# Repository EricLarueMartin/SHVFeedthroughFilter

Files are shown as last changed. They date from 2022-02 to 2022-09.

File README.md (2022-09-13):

# SHVFeedthroughFilter
Coaxial feedthrough filter that mounts on an SHV bulkhead.

SHV bulkhead connectors on both ends allow mounting the filter such that the body of the filter is on either side of the bulkhead, which may be helpful for space constraints.

Uses commercially available parts to make a high voltage filter that fits on a standard SHV bulkhead connector.
This filter was designed for use biasing cryogenically cooled solid state detectors, which have very low leakage current making high resistance series elements suitable.

Resistors are axial lead able to handle the high voltage while the sides of the resistor body are near ground, such as Ohmite MOX112523*. Though a shorter resistor would work the stray capacitance is important to performance and this model has the lowest stray capacitance at 0.25 pF.

Connector used for protoype was TE Connectivity AMP Connectors 5225059-3, this is out of production and an alternative will become necessary when stocks depleate. The BM61482 from Bracke Manufacturing appears to be a direct replacement. 

Capacitors are 6kV 2225 package, such as Vishay Vitramon HV2225*. Six 2.7 nF capacitors were used for the prototype, but three high capacitance X7R capacitors and three lower capacitance C0G capacitors would likely result in better high frequency performance.

The center piece for the capacitors to solder to is a brass standoff, 6 mm hex diameter and up to 6mm height.

The tube is a 0.686 inch ID brass or copper tube. A 3/4 inch 0.032 inch wall tube is readily available and suitable.

A bleeder resistor on the load side of this filter will result in voltage drop across the series resistors. Bleeder resistors are not required if stored energy is under 10 J. 

The prototype filter used six 2.7 nF capacitors, which will only result in 0.3 J of stored energy at 6 kV. With 100 Mohm series resistors the maximum current the filter can produce is only 60 microamps at 6 kV, which is negligible compared to the ~10 mA requires to produce a dangerous shock. With 0.25 pF of parallel capacitance this high of a resistance isn't effective at frequencies above 10 kHz. 5 Mohm resistors would still limit the current from a shock to ~ 1 mA and performance at power distribution frequencies would still be better than 100 dB.

The cable ground of the recommended connector acts as a guard ring to reduce the effective capacitance between leads of the axial resistors, this stray capacitance dominates filter performance in the GHz range. A guard ring is added using washers for the second stage resistor.

This version includes a second capacitor stage with a pulse line. This allows pulsing through the HV line and also provides source termination at the filter, which can help reduce noise that is picked up on the HV line after the filter.

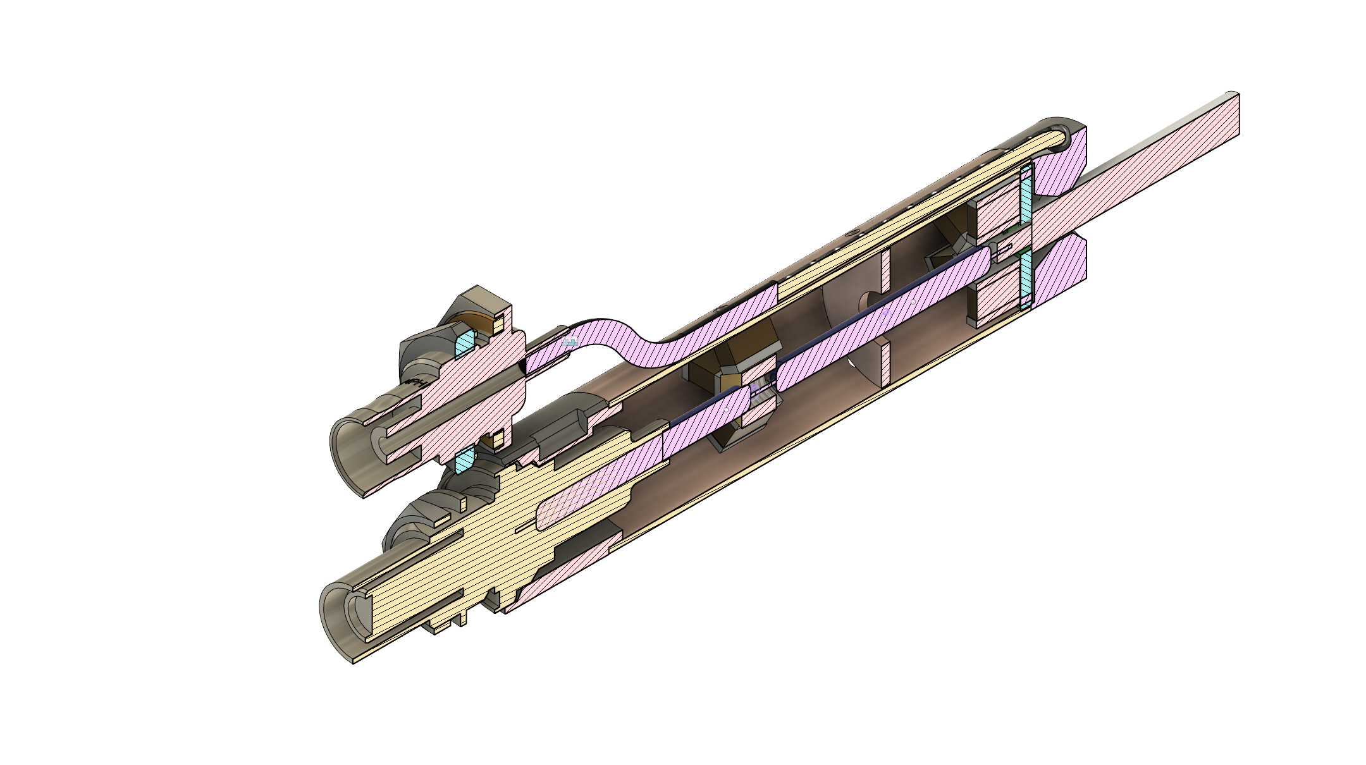
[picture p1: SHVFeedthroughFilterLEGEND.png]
SHV to SHV Feedthrough Filter


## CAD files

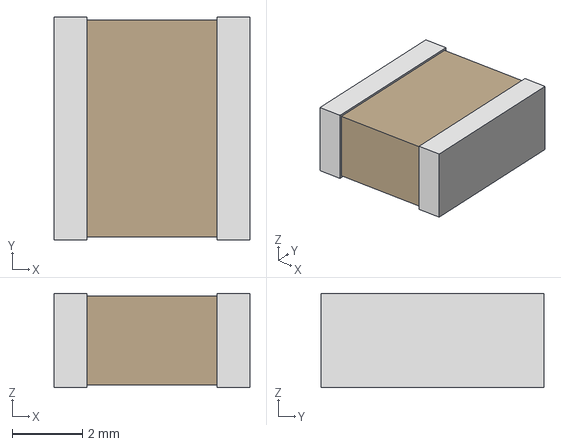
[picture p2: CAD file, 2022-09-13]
DesignFiles/SHV_Feedthrough_PulserPCB/CAP_HV2225_VIS.step
5.59 x 6.35 x 2.69 mm

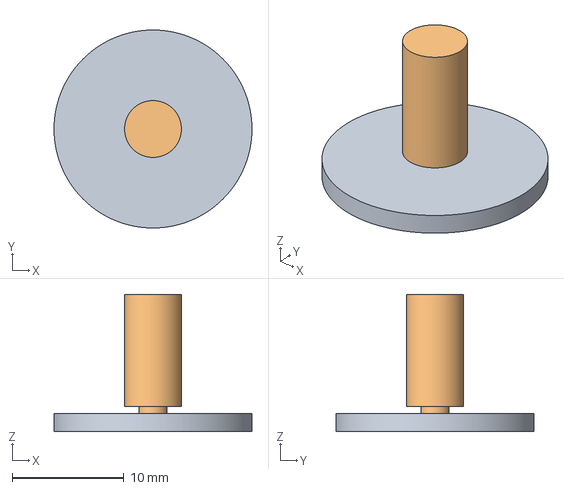
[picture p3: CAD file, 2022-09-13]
EpoxytestJig.3mf
17.7 x 17.7 x 12.3 mm
Shape-Cylinder x 2

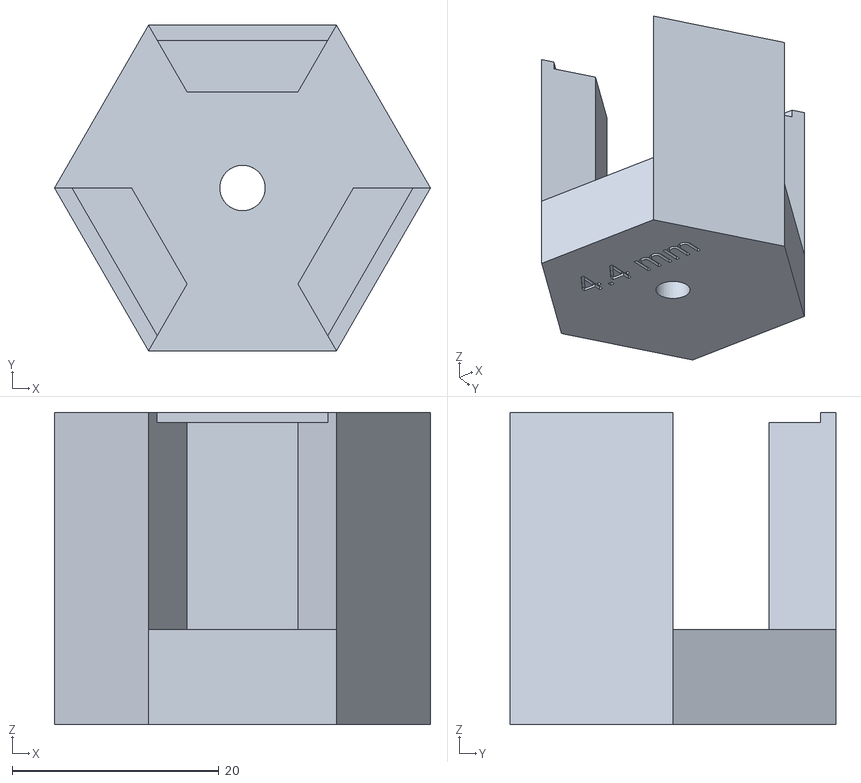
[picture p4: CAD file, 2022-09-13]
FabricationFiles/ResistorJig4.4mm.stl
36.4 x 31.5 x 30.2

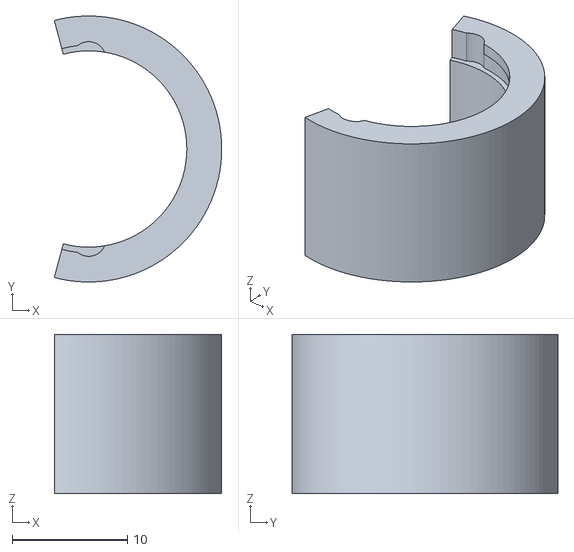
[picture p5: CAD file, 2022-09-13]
FabricationFiles/EndAlignmentJig.stl
14.5 x 23.0 x 13.8

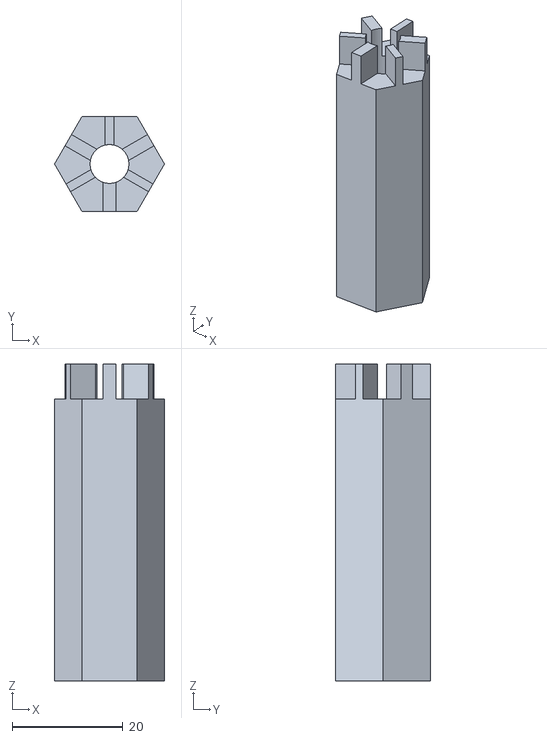
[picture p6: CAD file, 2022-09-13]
FabricationFiles/CapacitorRemovalJig.stl
19.8 x 17.2 x 57.1

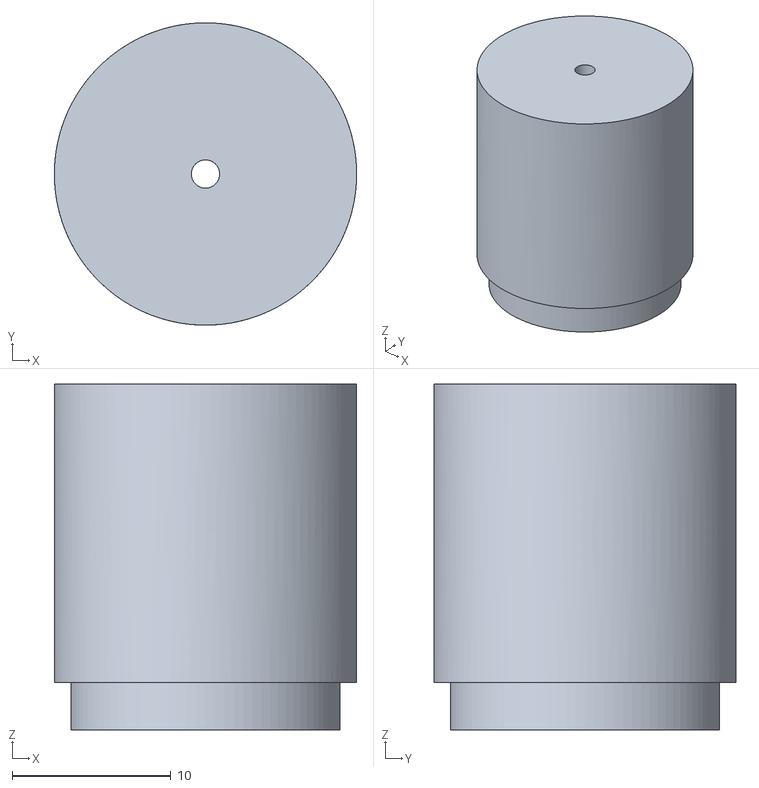
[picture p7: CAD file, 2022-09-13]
FabricationFiles/PinPositioningDuringEndCapAttachmentJig.stl
19.0 x 19.0 x 21.8

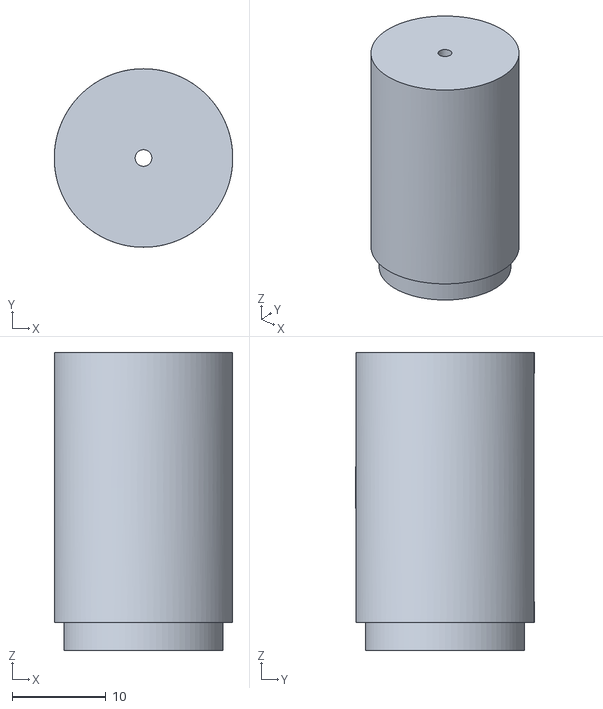
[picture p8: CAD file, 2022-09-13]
FabricationFiles/PinPositionCheckJig.stl
19.0 x 19.0 x 31.8

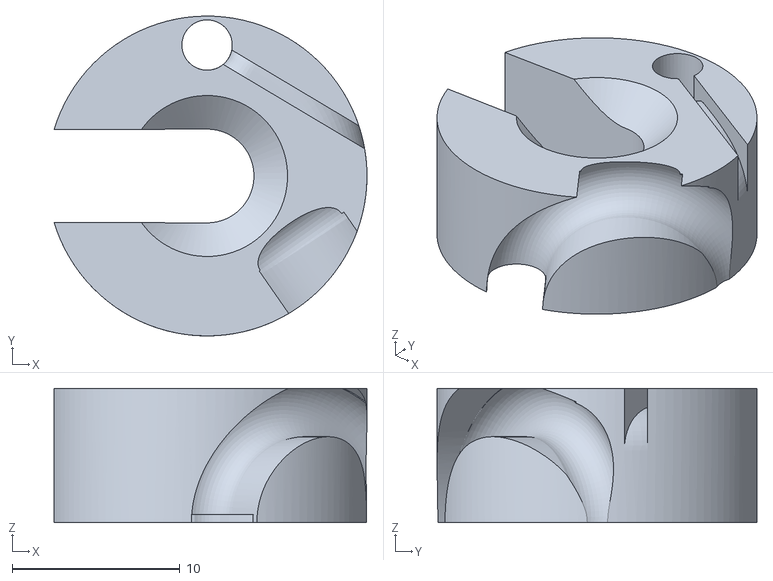
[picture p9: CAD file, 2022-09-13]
FabricationFiles/EndCap.stl
18.6 x 19.0 x 8.00

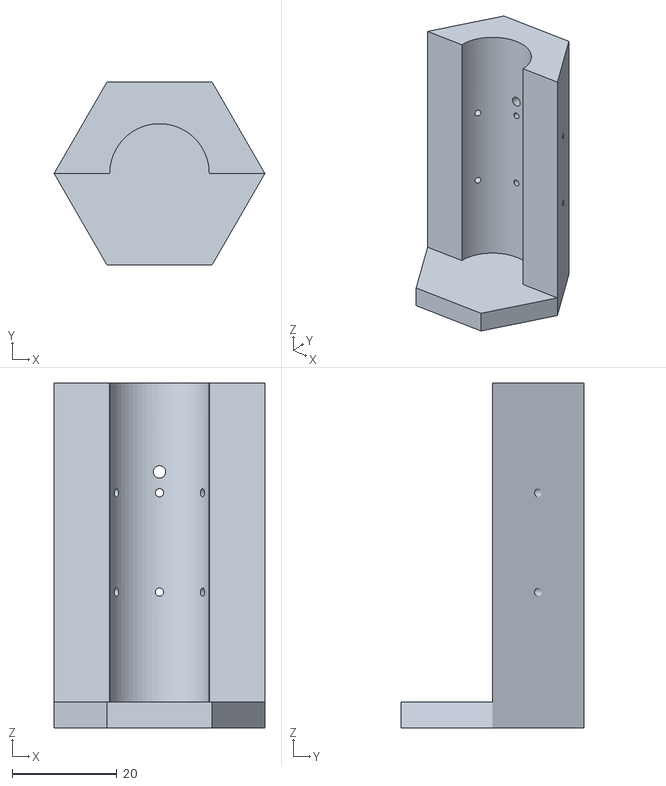
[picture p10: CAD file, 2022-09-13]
FabricationFiles/TwoPartTubeJigA.stl
40.3 x 34.9 x 66.0

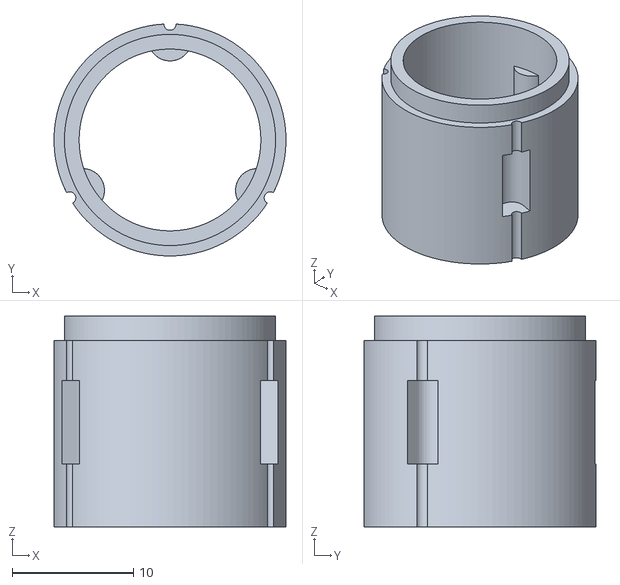
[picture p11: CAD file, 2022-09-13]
FabricationFiles/TubeInsulator+0.4mm.stl
19.1 x 19.1 x 17.4

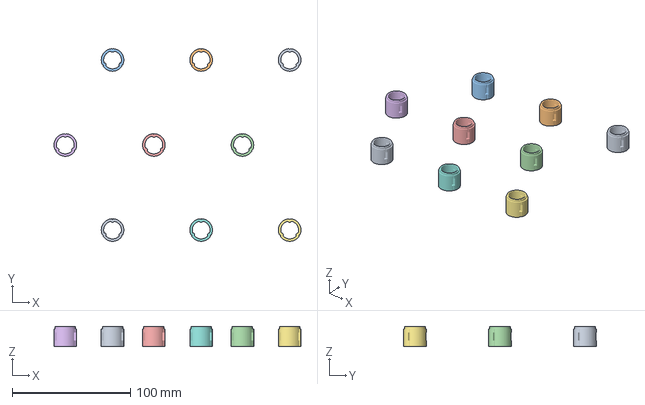
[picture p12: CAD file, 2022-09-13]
FabricationFiles/TubeInsulatorx9.3mf
209.1 x 163.1 x 17.0 mm

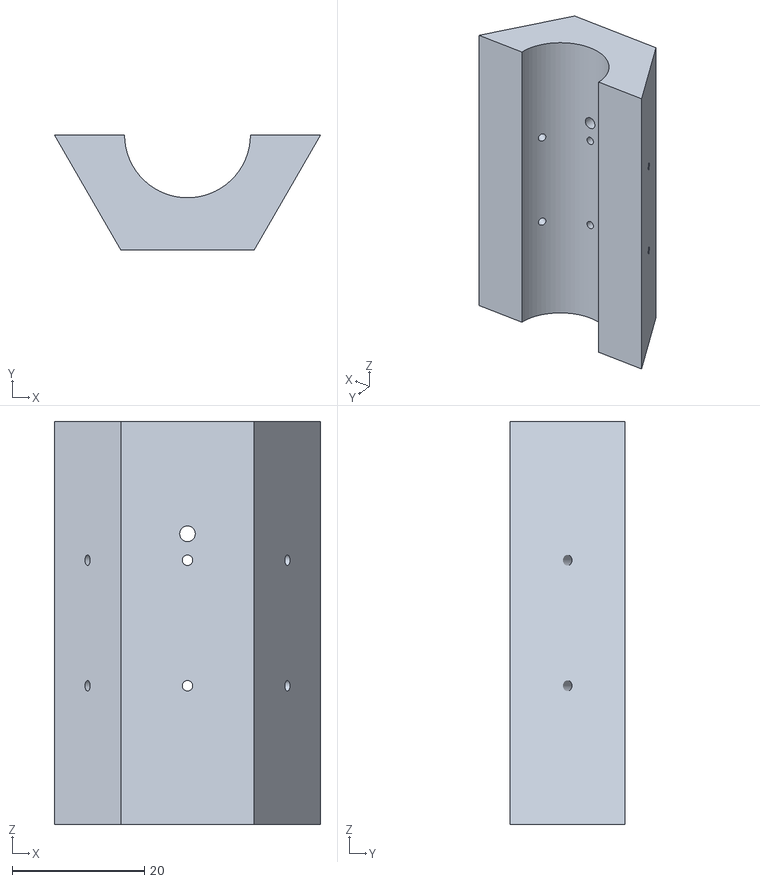
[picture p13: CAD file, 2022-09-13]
FabricationFiles/TwoPartTubeJigB.stl
40.3 x 17.5 x 61.0

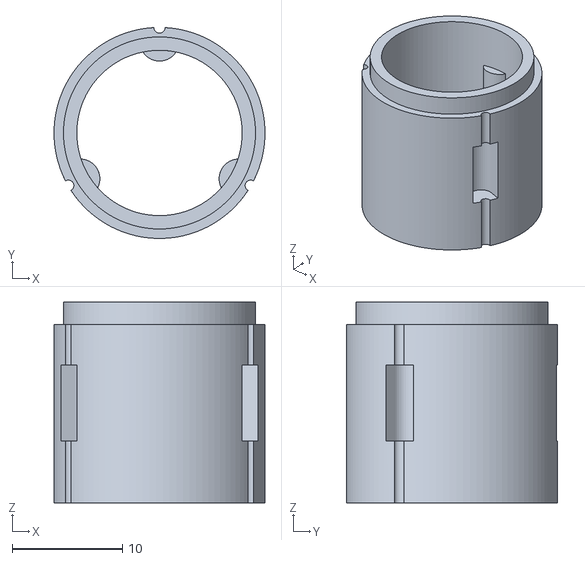
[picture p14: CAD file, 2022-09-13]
FabricationFiles/TubeInsulator+1.2mm.stl
19.1 x 19.1 x 18.2

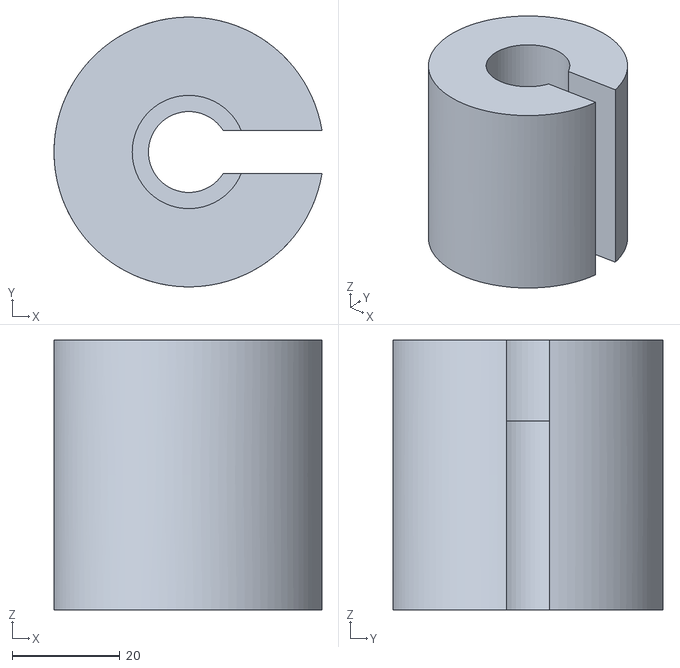
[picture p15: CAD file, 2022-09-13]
FabricationFiles/PottingStand.stl
49.7 x 50.0 x 50.0

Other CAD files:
FabricationFiles/ResistorJig4.0mm.stl
FabricationFiles/TubeInsulator.stl
FabricationFiles/TubeInsulator-2.0mm.stl
FabricationFiles/AluminumCapacitorJig.step
DesignFiles/SHVFeedthroughFilterWithPulseLine_LEGEND60.f3z
FabricationFiles/StandoffCuttingJig.stl
FabricationFiles/TubeInsulator+0.8mm.stl
FabricationFiles/TubeInsulator-0.4mm.stl
FabricationFiles/TubeInsulator-0.8mm.stl

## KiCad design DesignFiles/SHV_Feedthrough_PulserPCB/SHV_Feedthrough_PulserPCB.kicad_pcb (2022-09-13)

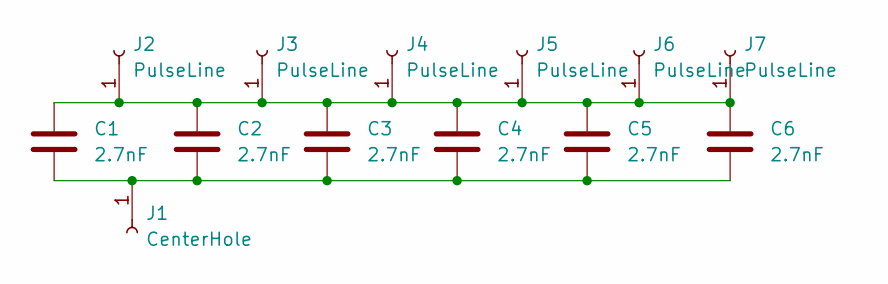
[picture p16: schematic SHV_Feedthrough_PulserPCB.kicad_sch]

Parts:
C1, C2, C3, C4, C5, C6: 2.7nF; HV2225SideMount
J1: CenterHole; MountingHole_2.1mm
J2, J3, J4, J5, J6, J7: PulseLine; RG-174MinHole

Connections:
unnamed: C1.1, C2.1, C3.1, C4.1, C5.1, C6.1, J2.1, J3.1, J4.1, J5.1, J6.1, J7.1
unnamed: C1.2, C2.2, C3.2, C4.2, C5.2, C6.2, J1.1

Board: 2 copper layers, 13 parts (0 on the bottom side), 2 nets, no tracks yet.

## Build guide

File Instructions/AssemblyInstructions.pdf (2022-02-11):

SHV coaxial feedthrough RCR lter
This details how to construct an SHV feedthrough lter using two high voltage series resistors and six parallel capacitors to ground. This lter is intended for use biasing germanium detectors for the LEGEND experiment where the load current is expected to be < 1 nA and a large series resistance is acceptable. The nal lter characteristics are 100 MΩ input resistance, 100 MΩ output resistance, and 16 nF capacitance to ground. The expected capacitance between input and output is 0.13 pF. The lter is constructed to minimize radiation power transfer by keeping the input on the same axis as the output, having the ground current symmetric about the output axis so grounding bypass capacitor radiation is canceled and is emitted perpendicular to the output axis. The entire lter is contained in a sealed tube that mounts on a front-side nut SHV bulkhead jack, which can be lled with oil.
Parts:
- 1 SHV bulkhead jack, TE Connectivity AMP Connectors 5225059-3
- 1 3/4 OD 0.032 wall copper 101 tube cut to 3.16
- 6 2.7 nF 6 kV ceramic capacitors, Vishay Vitramon HV2225Y272KX6ATHV
- 1 0.625 OD 0.26 ID copper washer 1
- 1 5.5 mm brass hex stando cut to 0.25 1
- 2 100 MΩ 7.5 kV axial lead resistors, Ohmite MOX1125231006FE

1

1Appropriate sizes for some components were unavailable.

1

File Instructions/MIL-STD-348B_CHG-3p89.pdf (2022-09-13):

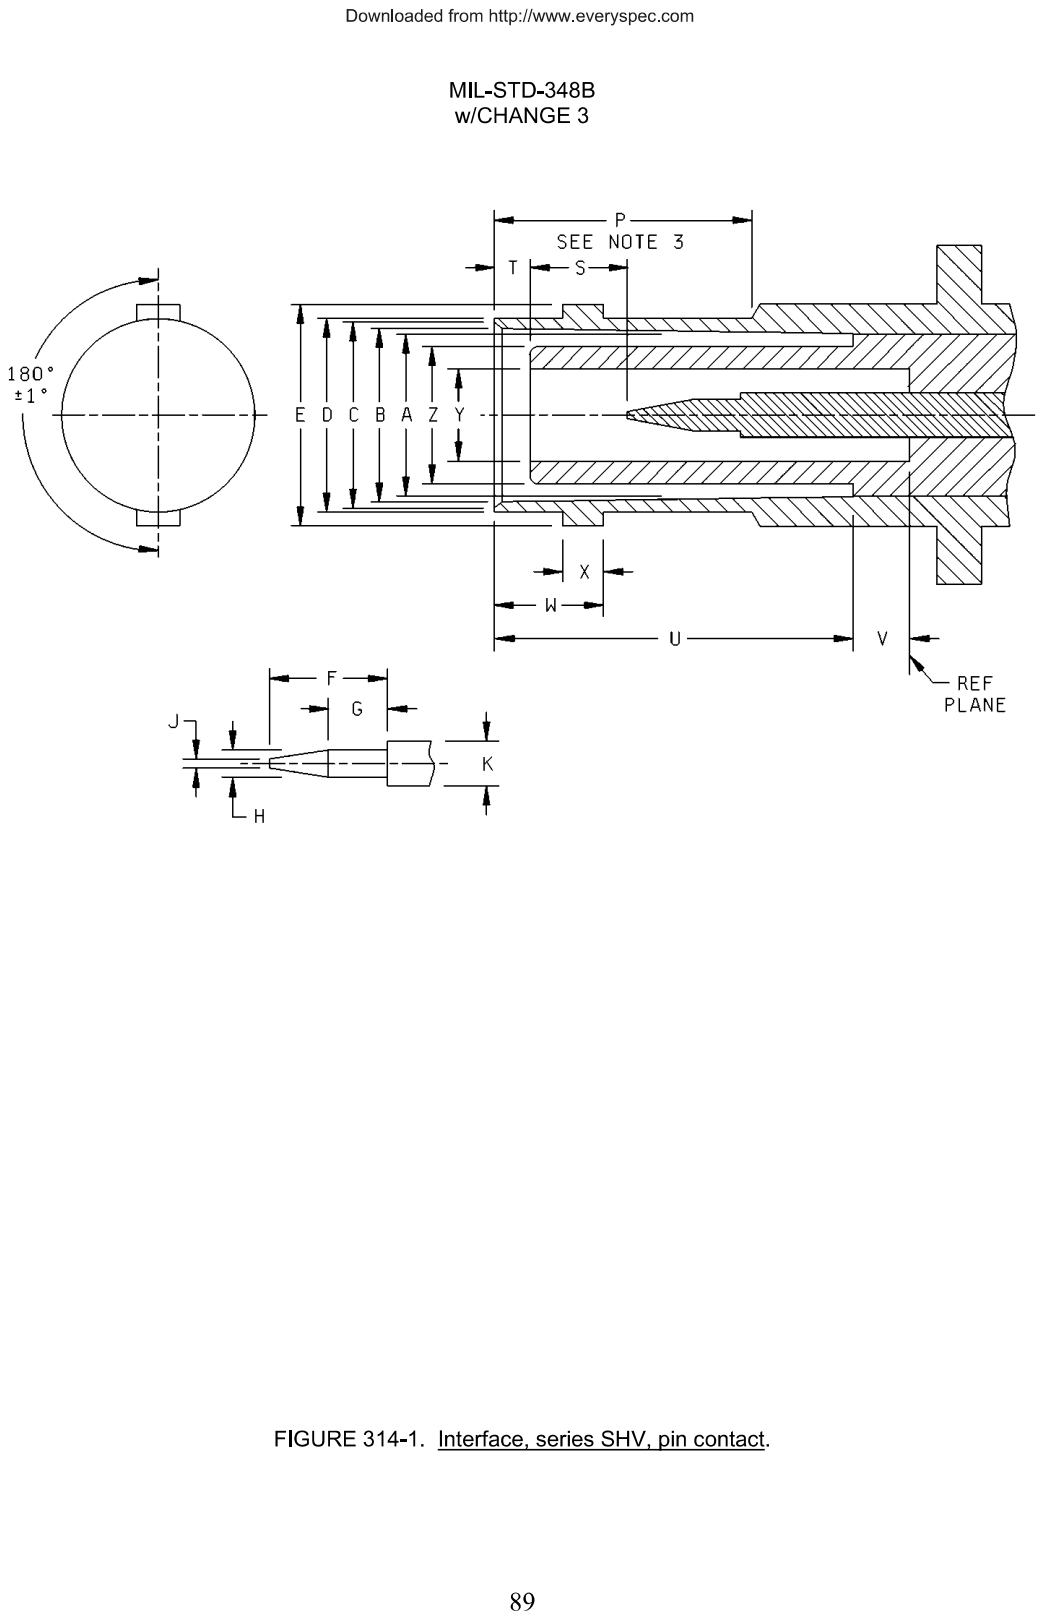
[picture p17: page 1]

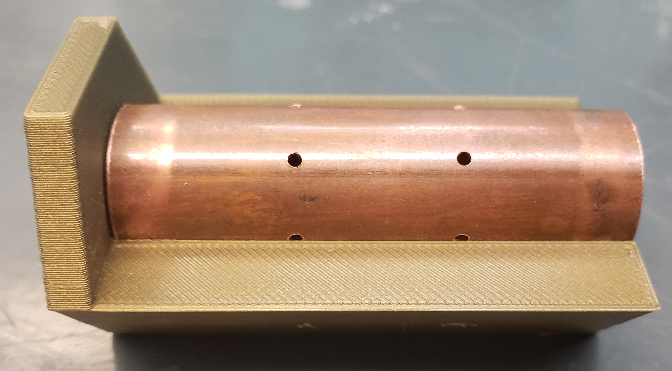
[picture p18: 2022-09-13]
Instructions/TubeRotatedInJig.jpg

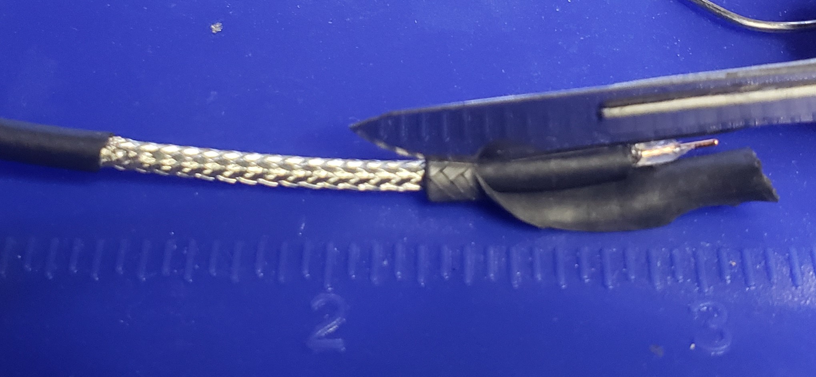
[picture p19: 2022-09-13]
Instructions/TrimmingJacketOffCable.jpg

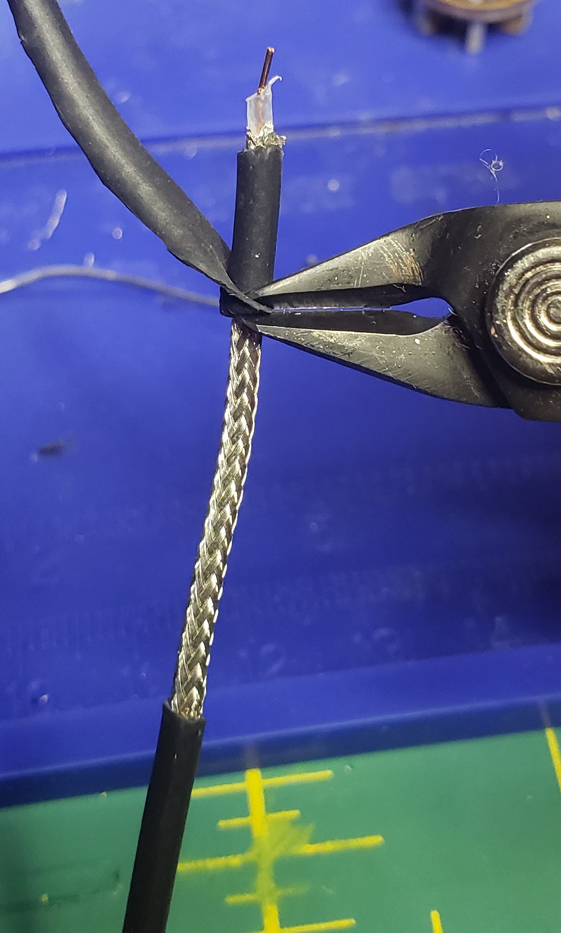
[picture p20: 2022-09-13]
Instructions/ClippingJacket.jpg

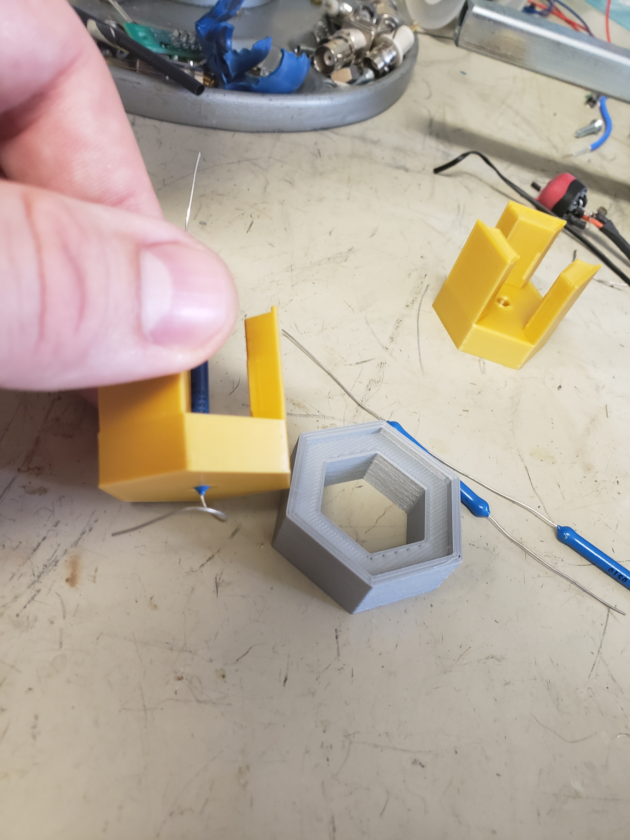
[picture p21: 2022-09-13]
Instructions/ResistorSpringLead.jpg

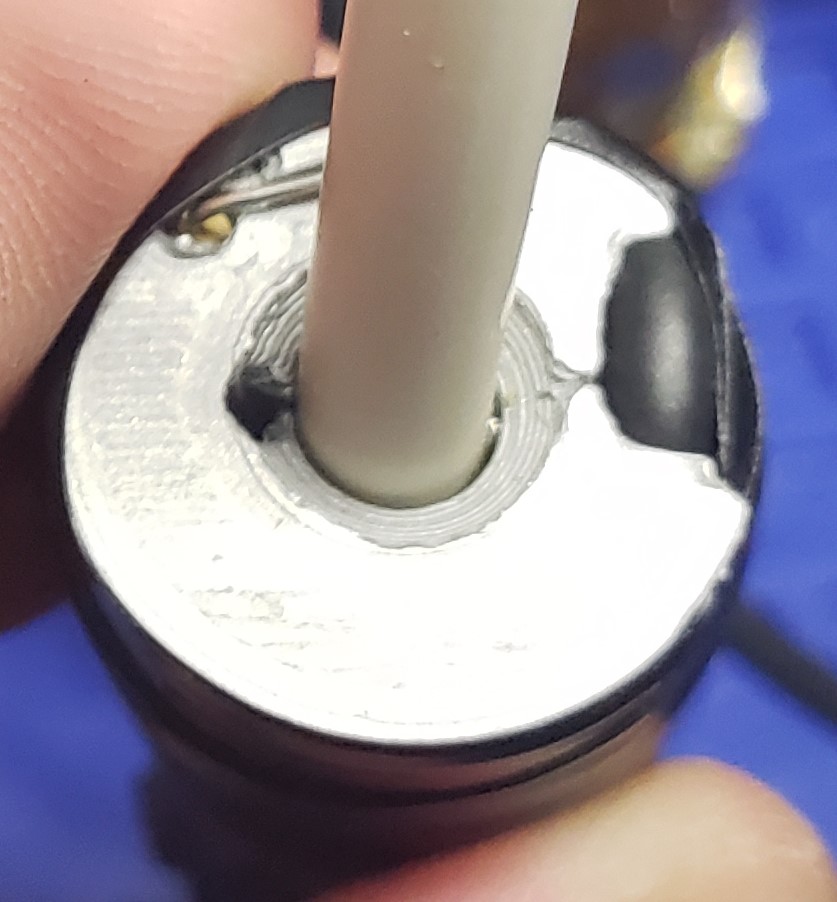
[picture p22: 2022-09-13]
Instructions/EndCapFillPort.jpg

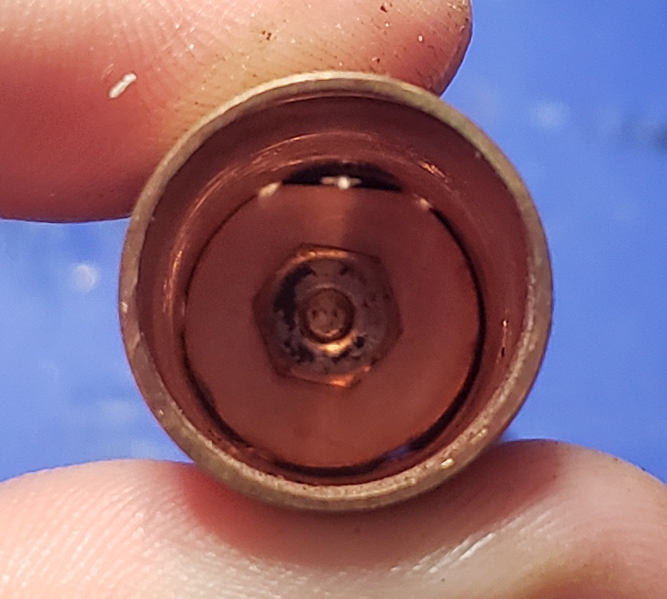
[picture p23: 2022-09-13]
Instructions/WasherRotation.jpg

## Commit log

2022-02-08 Added jigs.
    [2PartTubeJig.f3d, CapacitorJig.f3d, SHVFeedthroughFilter v8.f3z, SHVFeedthroughFilter.f3z]
2022-02-10 Added STLs for jigs, data sheets, and LTspice simulation.
    [2PartTubeJigA.stl, 2PartTubeJigB.stl, CAP_HV2225_VIS.step, CapacitorJig.stl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]
2022-02-13 Reorganized directory structure. Minor changes to some files.
    [2PartTubeJig.f3d, 2PartTubeJigA.stl, 2PartTubeJigB.stl, CapacitorJig.f3d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]
2022-02-20 Completed first draft of instructions.
    [2PartTubeJigA.stl, 2PartTubeJigB.stl, CapacitorJig.stl, Grommet.stl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]
2022-02-24 Added versions with two SHV jacks and with more common SHV jacks using adapters.
    [CapacitorJig.stl, DoubleSHVFeedthroughFilterUsingAdapters.f3z, Grommet.stl, SHVBulkheadAdapter.step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]
2022-02-25 Data sheet for replacement connector from Bracke Manufacturing.
2022-02-26 Slight modification to capacitor jig. Added multi-body files for 3D printing intended for individual part completion.
    [CapacitorJig.f3d, CapacitorJig.stl, CapacitorJigx9.3mf, TubeJig.3mf]
2022-02-26 Added construction image of resistor.
2022-02-26 Added simulation outputs and 16 grommet individual object completion file for 3D printing.
    [GrommetX16.3mf]
2022-03-03 Photo of prefilter on LEGEND filter
2022-03-03 File to printing 9 jigs one at a time
    [CapacitorJigx9.3mf]
2022-03-20 Updated Performance
    [DoubleSHVFeedthroughFilterUsingAdapters.f3z, SHVConnectorPullTool.stl, TubeJig.3mf, TubeJigDoubleSHVTrimmedPartA.stl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]
2022-06-27 Added second capacitor stage with pulse line.
    [CAP_HV2225_VIS.step, CapacitorJig.f3d, CapacitorJig.stl, CapacitorJig2.7nF470pF.f3d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]
2022-07-12 Version for LEGEND, with separate grounds for input and filter connected by resistor.
    [ConnectorStandJig.f3d, EndCap.stl, PulseCouplingCapacitorJig.f3d, ResistorJig4.4mm.stl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]
2022-07-12 Removed PCB jig, use resulted in breaking resistors.
    [PulseCouplingCapacitorJig.stl]
2022-07-12 Added design file.
    [SHVFeedthroughFilterLEGEND.step]
2022-07-13 Added files for printing.
    [CapacitorJig2.7nF470pF.stl, CapacitorJig2.7nF470pFx9.3mf, EndCapx9.3mf, TubeInsulatorx9.3mf]
2022-07-13 Modified tube hole position. Small change to end cap design.
    [EndCap.stl, EndCapx9.3mf, SHVFeedthroughFilterLEGEND.stl, SHVFeedthroughFilterLEGEND.stp]
2022-08-04 Added more jigs and updated instructions to make assembly easier.
    [AluminumCapacitorJig.step, CapacitorJig2.7nF470pF.stl, CapacitorJig2.7nF470pF4-40.stl, CapacitorJig2.7nF470pF4-40x9.3mf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]
2022-08-04 Added solder recommendations and reformatted parts list.
    [PinPositioningDuringEndCapAttachmentJig.stl]
2022-08-09 Modified instructions.
    [CapacitorJig2.7nF470pF4-40.stl, CapacitorJig2.7nF470pF4-40x9.3mf, CapacitorJig2.7nF470pFx9.3mf, CapacitorRemovalJig.stl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]
2022-08-11 Updated instructions to include ensuring MIL-STD-348B_CHG-3 conformity.
    [AluminumCapacitorJig.step, CapacitorJig2.7nF470pF.f3d, EndAlignmentJig.stl, PinPositionCheckJig.stl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]
2022-09-12 Added slots to pulser board. Updated instructions for cleaning.
    [EndCap.stl, EndCapx9.3mf, EpoxytestJig.3mf, PottingStand.stl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]
